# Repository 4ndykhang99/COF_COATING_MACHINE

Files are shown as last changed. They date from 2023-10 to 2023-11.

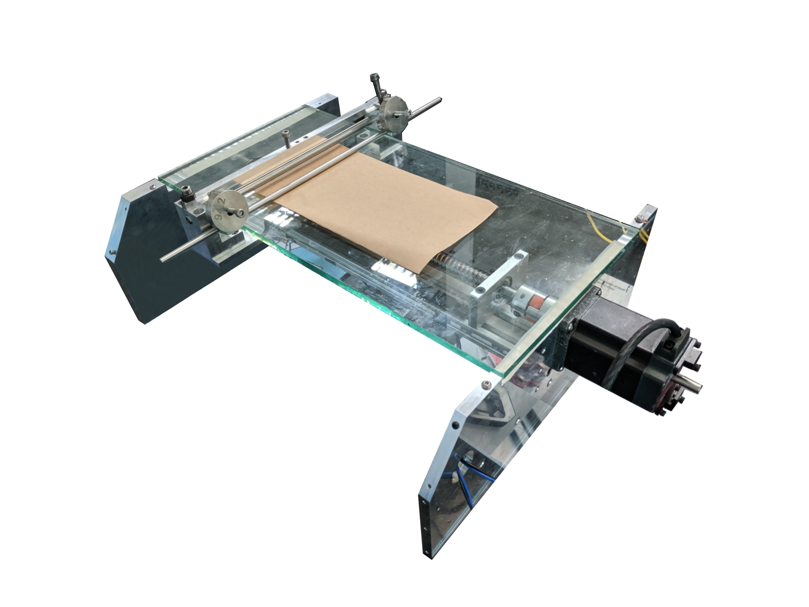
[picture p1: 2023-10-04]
3. Report/23_02_2023 - Introductrion about Lab Coating _ COF machine/1.png

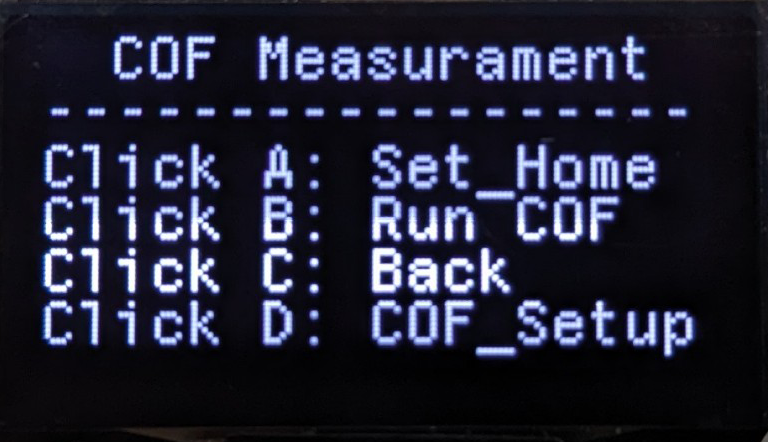
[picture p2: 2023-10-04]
4. Hình/HMI/5.png

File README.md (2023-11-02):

# COF_COATING_MACHINE
Included code, PCB, Software for COF &amp; Coating machine

## 11/2/2023
- Ghi nhận các lỗi:
    - Trôi công tắc hành trình trong chế độ COF.
    - Khi sử dụng COFcontroller.exe lưu đến mẫu 9 hoặc 10 sẽ bị lỗi ( chưa xác định), dữ liệu bị ngắn đi khi plot biểu đồ trên phần mềm, hoặc có thể do tốc độ của motor nhanh dần lên, càng đo về sau, biểu đồ plot lên càng ngắn.
    - Lỗi random: đo COF, bộ điều khiển trả về giá trị 0. Phần mềm lẫn board đọc về giá trị 0.
    - Idea về detect vị trí mỗi lần khởi động máy: khởi tạo một hàm scan_pos(), mỗi khi mất điện và bật hệ thống lại, hoặc mỗi lần reset, chương trình sẽ qua hàm scan_pos để nhận biết trạng thái của 2 công tắc hành trình như thế nào => giải quyết được vấn đề lưu vào bộ nhớ flash.
    - Lỗi liên quan đến cơ khí: Ở các màng mỏng có độ nhám cao, các kẹp base không thể giữ được hoàn toàn màng được đo, dẫn đến khi sled càng về cuối màng, màng càng bị nhăng -> kết quả đo sẽ sai lệch.
    - Anh Thiện suggest biểu đồ tự động detect chiều cao và tự động scale vừa với cửa sổ biểu đồ.

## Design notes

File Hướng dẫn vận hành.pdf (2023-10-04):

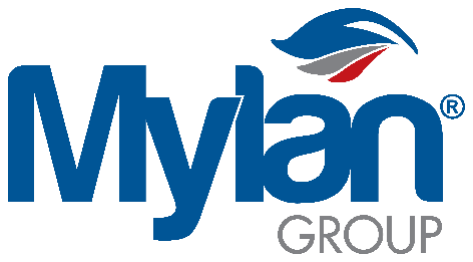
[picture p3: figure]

THIẾT BỊ ĐO HỆ SỐ MA SÁT VÀ TRÁNG MÀNG

MÃ THIẾT BỊ: MOP_CC2_0001

HƯỚNG DẪN VẬN HÀNH

Address: Longduc Industrial Park Travinh City, Travinh Province, Vietnam

Email: info@mylangroup.com

Phone: +84 -294-3846-997

## MỤC LỤC

THÔNG SỐ THIẾT BỊ | 3
CHỨC NĂNG MÁY | 3
CẤU TRÚC MÁY (COF) | 4
CẤU TRÚC MÁY ( COATING) | 5
GIÁ TRỊ LOADCELL | 6
KEYPAD | 6
ĐIỀU KHIỂN CHẾ ĐỘ TRÁNG GIẤY (COATING) | 7
ĐIỀU KHIỂN CHẾ ĐỘ ĐO HỆ SỐ MA SÁT (COF) | 7
CHANGE COF SPEED: ĐIỀU CHỈNH TỐC ĐỘ ĐO COF | 9
CHANGE COF DISTANCE: ĐIỀU CHỈNH KHOẢNG CÁCH ĐO COF | 9
SET ZER0: ĐƯA BỘ ĐIỀU KHIỂN LOADCELL VỀ ZERO | 9
HƯỚNG DẪN CHUẨN BỊ MẪU ĐO HỆ SỐ MA SÁT | 10
1. Cắt mẫu theo Sled: Chiều rộng là MD, dài là CD | 10
2. Cắt mẫu cho Base kẹp màng: chiều dài là MD, rộng là CD | 11
3. Đặt đúng mặt cần đo cho Sled | 11
4. Cố định một đầu màng trên Sled bằng băng keo dính | 12
5. Hoàn thành kẹp màng cho Sled | 12
HƯỚNG DẪN THỰC HIỆN ĐO HỆ SỐ MA SÁT | 13
1. Kẹp màng cho Base | 13
2. SetHome cho base | 13
3.Bắt đầu đo COF | 14
ĐIỀU KHIỂN MÁY COF COATING THÔNG QUA MÁY TÍNH | 15
1. Cài đặt phần mềm: | 15
2. Cách sử dụng chương trình | 15
3. Chế độ COATING | 15
4. Chế độ đo COF | 17
XEM KẾT QUẢ VÀ XUẤT PDF | 19
MÔ TẢ KẾT QUẢ ĐO HỆ SỐ MA SÁT | 20
1. STATIC | 20
2. KINETIC | 20

THÔNG SỐ THIẾT BỊ

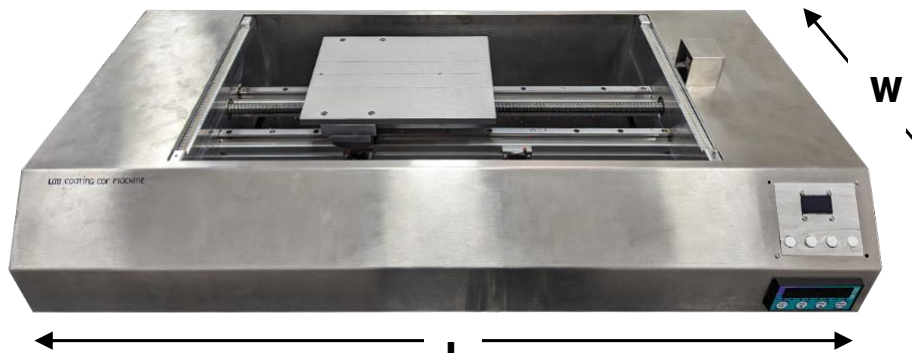
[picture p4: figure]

Điện áp đầu vào | 220VAC, 50/60Hz, 5amp
Nhiệt độ vận hành | 16 – 70 Độ C
Tốc độ | 0.1 – 4m/ phút
Khối lượng Sled | 200g
Thông số kích thước thân máy | 950x550x165mm (LxWxH)
Thông số base đặt màng COF | 250x200mm (LxW)
Thông số base Coating | 600x285mm (LxW)

CHỨC NĂNG MÁY

- Tích hợp tính năng Coating và đo hệ số ma sát trên cùng thiết bị.
- Màn hình hiển thị trực quan, dễ dàng điều khiển.
- Trang bị LoadCell tải trọng 600g với độ lệch chuẩn 0.2%.
- Có khả năng thu thập dữ liệu đo hệ số ma sát và xuất PDF thông qua truyền thông USBCDC.
- Hỗ trợ phần mềm điều khiển và thu thập dữ liệu thông qua máy tính.

H

L

CẤU TRÚC MÁY (COF)

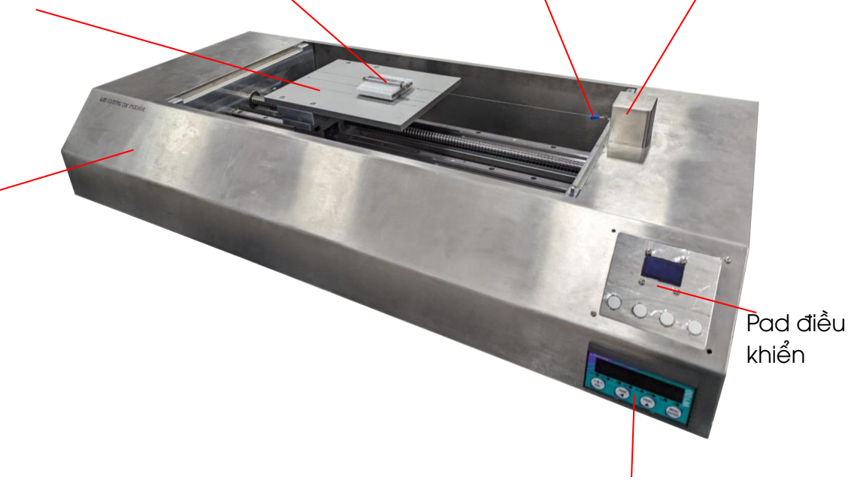
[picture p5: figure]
Pad điều khiển

- Switch nguồn: nằm phía sau Cover, dùng để bật tắt nguồn điện cho máy.
- Sled: Bao gồm khối vuông bao bởi Foam sốp với tổng khổi lượng 200g, dùng để gá màng vào và trượt trên màng cùng loại kẹp trên base kẹp màng COF.
- LoadCell: Đo lực kéo khi đang xác định hệ số ma sát của các tấm màng.
- Bộ điều khiển LoadCell: Thiết bị dùng để calib và chuyển đổi năng lượng nhận được từ LoadCell sang khối lượng.
- Pad điều khiển: Bao gồm 4 nút nhấn và một màn hình hiển thị, dùng để điều khiển và hiện thị công năng đang thực thi.
- Cover: Tấm kim loại bảo vệ và cách ly các thiết bị bên trong.

Sled

Dây kéo Sled

Base kẹp
màng COF

Cover

Loadcell

Bộ điều khiển
Loadcell

CẤU TRÚC MÁY ( COATING)

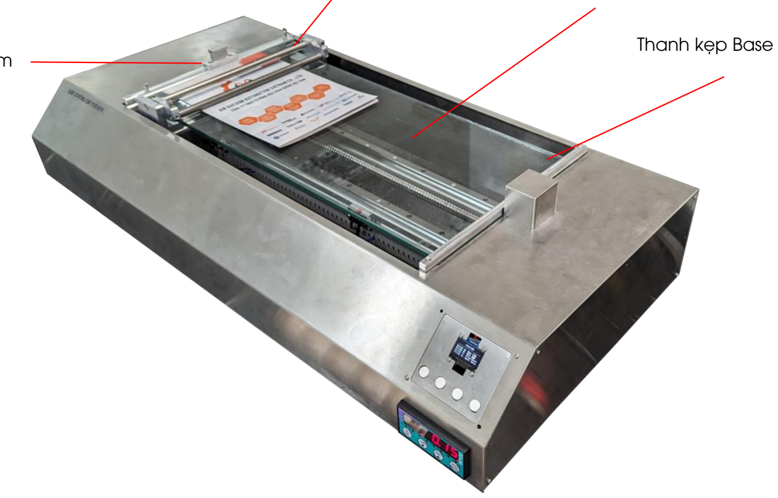
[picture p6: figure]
Thanh kẹp Base

- Thanh kẹp Film: Gồm có một dãy ron cao su và lò xo 2 bên, giúp thanh kim loại có thể đè, nén và giữ bề mặt Film cần coat không bị chạy.
- Module mayer bar: là bộ phận liên kết thanh trượt vitme với thanh mayer bar của máy.
- Coating Base: là vị trí đặt màng film cần coat, bề mặt làm bằng thủy tinh nên có độ nhẵn cao, nhược điểm dễ vỡ.
- Thanh kẹp Base: có 2 thanh kẹp base, giúp giữ Coating base ở 2 đầu.

Module mayer bar

Thanh kẹp Film

Coating Base

GIÁ TRỊ LOADCELL

- Giá trị được hiển thị trên Bộ điều khiển LoadCell, chính là giá trị qui đổi lực được kéo từ LoadCell.
- Giá trị an toàn mà LoadCell trên máy đo hệ số ma sát có thể kéo được không quá 600g.
- Nếu vượt ngưỡng giá trị an toàn, LoadCell có thể bị biến dạng, khiến các lần đo tiếp theo không đạt độ chính xác như ban đầu.

KEYPAD

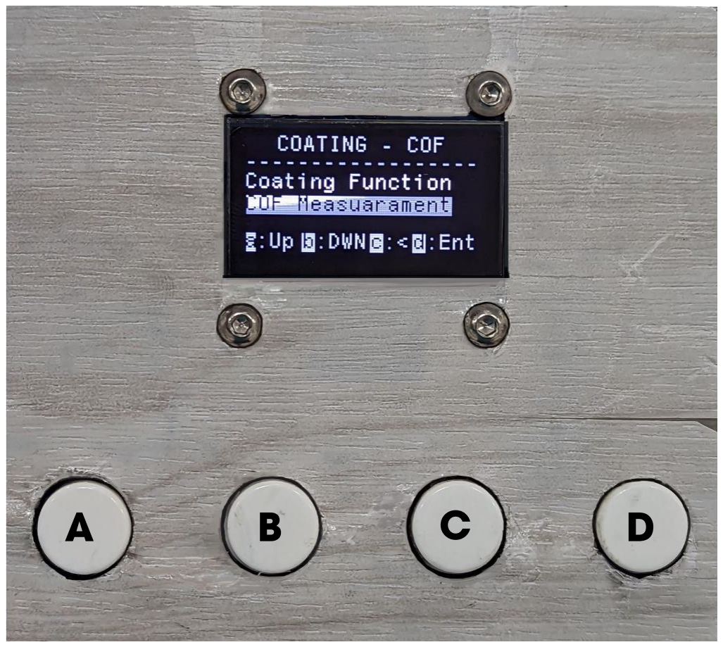
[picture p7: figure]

- KeyPad bao gồm màn hình Oled 1.3 inch và 4 nút nhấn A, B, C, D.
- Tùy vào từng giao diện điều khiển trên màn hình Oled mà các nút nhấn sẽ có các chức năng khác nhau.

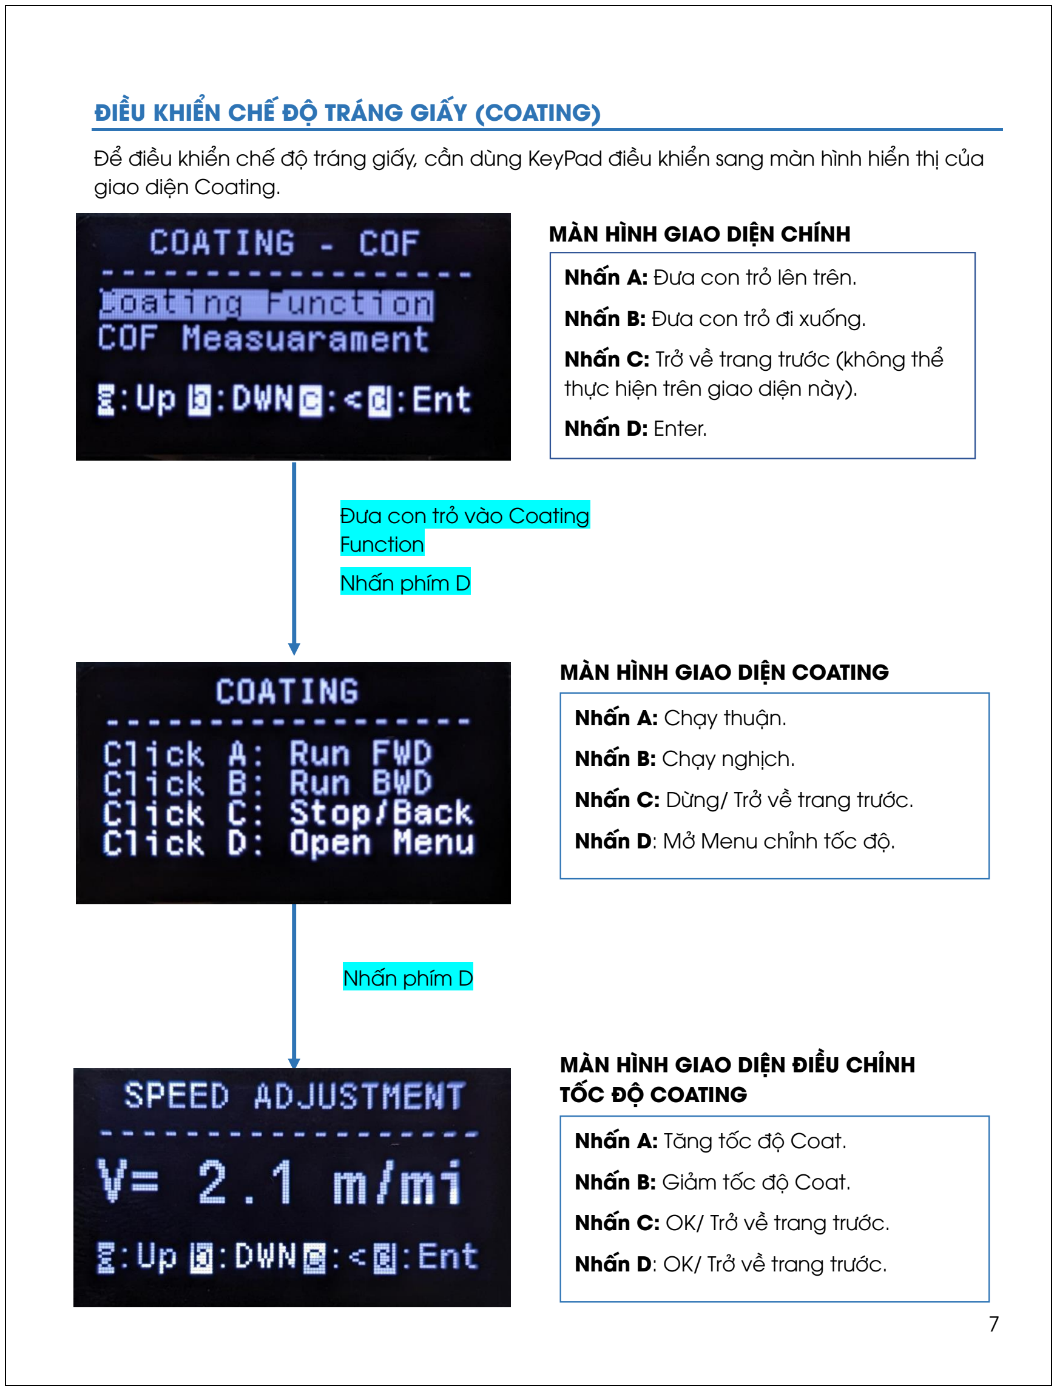
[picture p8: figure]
ĐIỀU KHIỂN CHẾ ĐỘ TRÁNG GIẤY (COATING); giao diện Coating.; Nhấn A: Đưa con trỏ lên trên.; Nhấn B: Đưa con trỏ đi xuống.; Nhấn C: Trở về trang trước (không thể; thực hiện trên giao diện này).; Nhấn D: Enter.; Nhấn A: Chạy thuận.; Nhấn B: Chạy nghịch.; Nhấn C: Dừng/ Trở về trang trước.; Nhấn D: Mở Menu chỉnh tốc độ.; MÀN HÌNH GIAO DIỆN CHÍNH; Nhấn phím D; MÀN HÌNH GIAO DIỆN COATING; MÀN HÌNH GIAO DIỆN ĐIỀU CHỈNH; TỐC ĐỘ COATING; Nhấn A: Tăng tốc độ Coat.; Nhấn B: Giảm tốc độ Coat.; Nhấn C: OK/ Trở về trang trước.; Nhấn D: OK/ Trở về trang trước.; Đưa con trỏ vào Coating; Function

Để điều khiển chế độ tráng giấy, cần dùng KeyPad điều khiển sang màn hình hiển thị của

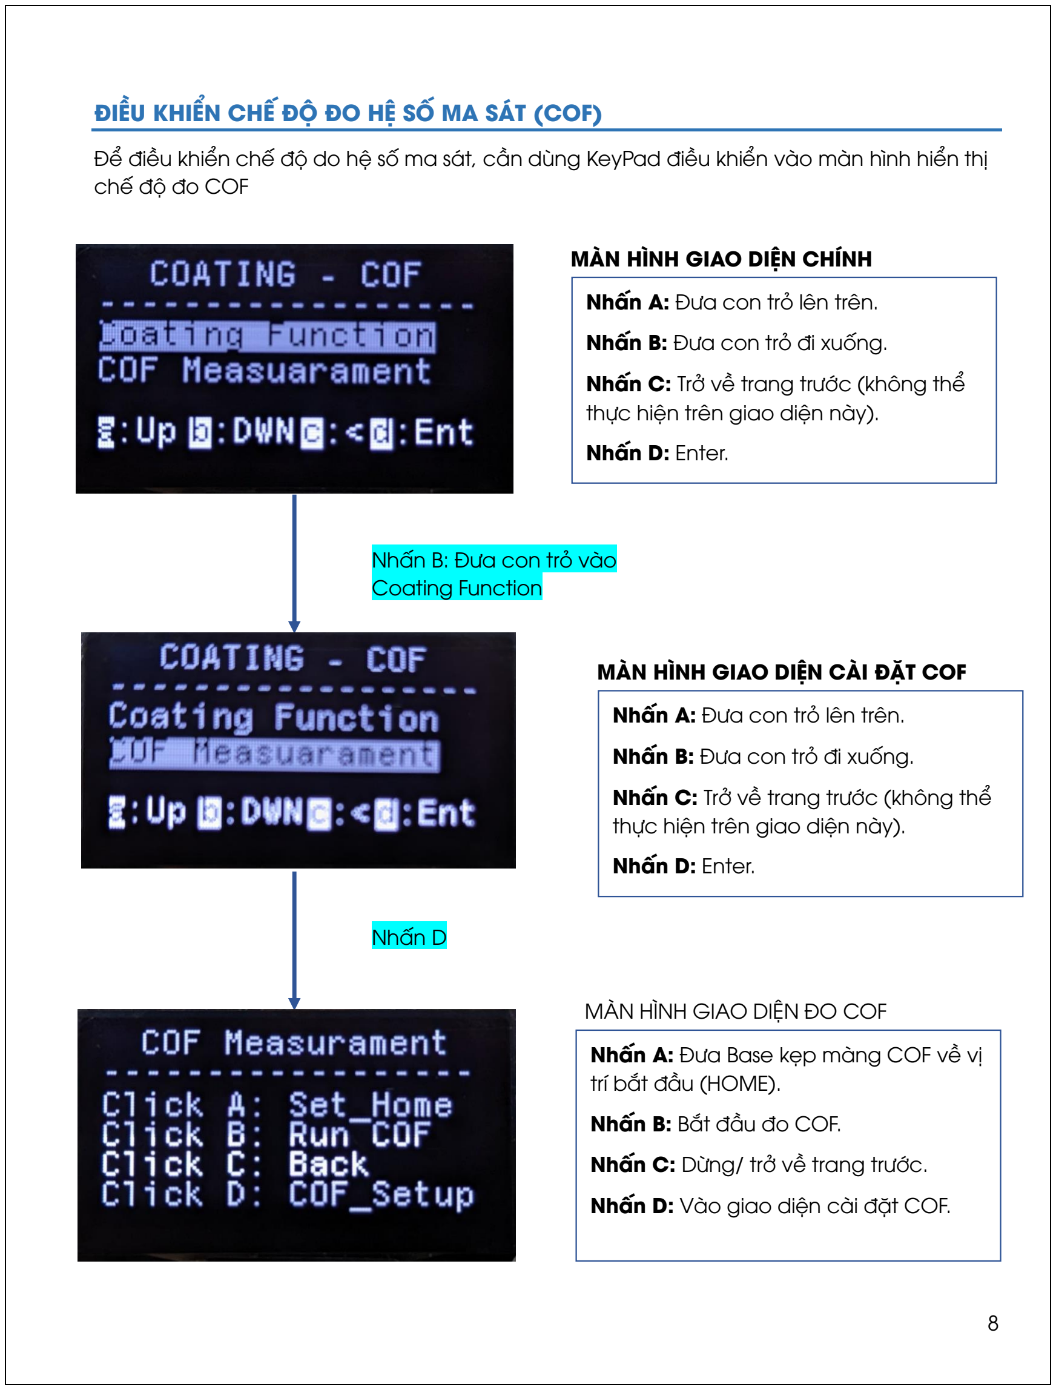
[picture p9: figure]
ĐIỀU KHIỂN CHẾ ĐỘ ĐO HỆ SỐ MA SÁT (COF); chế độ đo COF; MÀN HÌNH GIAO DIỆN CHÍNH; Nhấn A: Đưa con trỏ lên trên.; Nhấn B: Đưa con trỏ đi xuống.; Nhấn C: Trở về trang trước (không thể; thực hiện trên giao diện này).; Nhấn D: Enter.; Nhấn B: Đưa con trỏ vào; Coating Function; Nhấn D; Nhấn A: Đưa Base kẹp màng COF về vị; trí bắt đầu (HOME).; Nhấn B: Bắt đầu đo COF.; Nhấn C: Dừng/ trở về trang trước.; Nhấn D: Vào giao diện cài đặt COF.; MÀN HÌNH GIAO DIỆN ĐO COF; MÀN HÌNH GIAO DIỆN CÀI ĐẶT COF

Để điều khiển chế độ do hệ số ma sát, cần dùng KeyPad điều khiển vào màn hình hiển thị

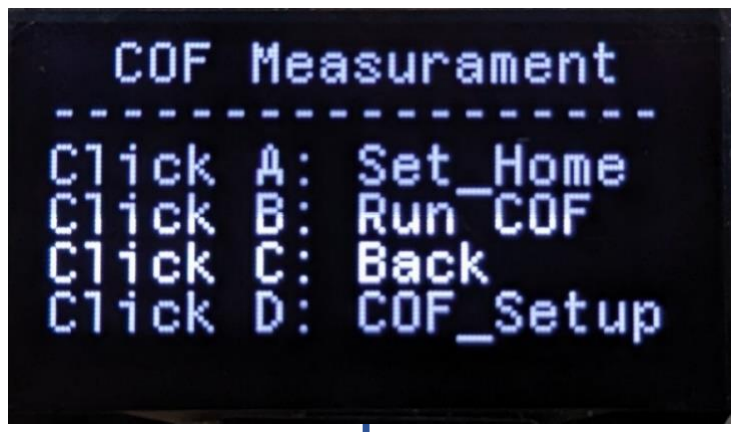
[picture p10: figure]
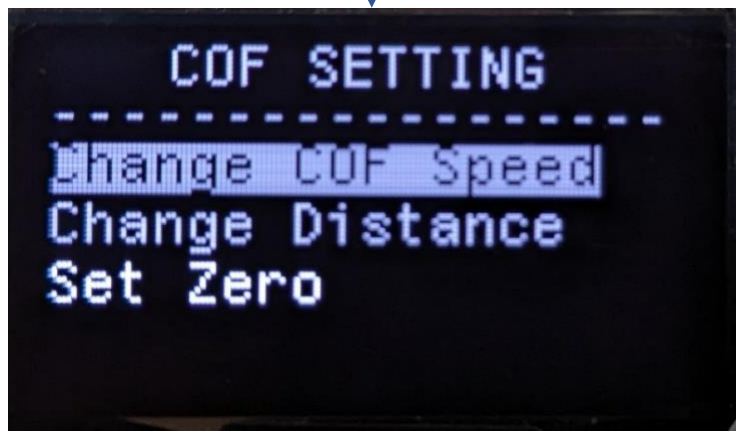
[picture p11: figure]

CHANGE COF SPEED: ĐIỀU CHỈNH TỐC ĐỘ ĐO COF

- Cách thức vào giống như điều chỉnh tốc độ Coating.
- Có 3 mức tốc độ: 0.10, 0.15 (Mặc định), 0.20 m/phút.

CHANGE COF DISTANCE: ĐIỀU CHỈNH KHOẢNG CÁCH ĐO COF

- Cách thức vào giống như điều chỉnh tốc độ Coating.
- Có 3 mức khoảng cách: 130 (Mặc định),140, 150 mm
SET ZER0: ĐƯA BỘ ĐIỀU KHIỂN LOADCELL VỀ ZERO

Sử dụng trong trường hợp khi chuẩn bị đo COF (dây kéo sled không căng) mà LoadCell đo được khác 0.

Lưu ý: Khi SetZero, dây kéo sled phải lỏng, chùng, không được căng.

Nhấn A: Đưa Base kẹp màng COF về vị trí bắt đầu (HOME).

Nhấn B: Bắt đầu đo COF.

Nhấn C: Dừng/ Trở về trang trước.

Nhấn D: Vào giao diện cài đặt COF.

MÀN HÌNH GIAO DIỆN ĐO COF

Nhấn D

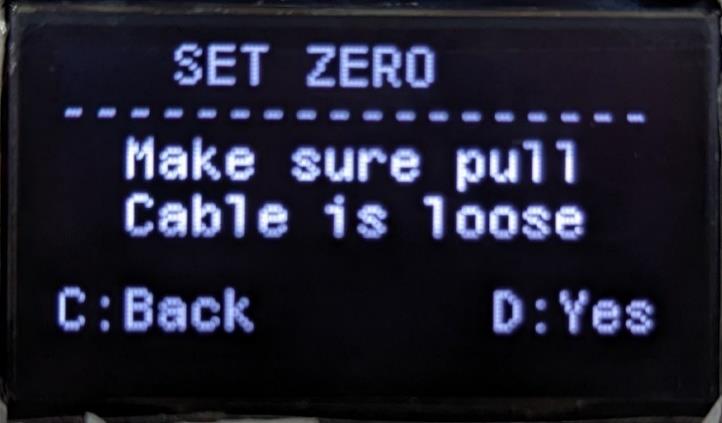
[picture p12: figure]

- Sau khi SetZero, hệ thống sẽ tự khởi động lại để bảo đảm mọi thứ hoạt động tốt nhất.

HƯỚNG DẪN CHUẨN BỊ MẪU ĐO HỆ SỐ MA SÁT

### 1. Cắt mẫu theo Sled

- Chú ý: tránh động tay vào phần cần đo để hạn chế tạp chất từ tay dính lên bề mặt.
- Quan trọng: Chiều rộng dưỡng Sled là MD, chiều dài là CD.

MÀN HÌNH GIAO DIỆN SETZERO

Nhấn C: Trở về trang trước, hủy bỏ SetZero

Nhấn D: Đã kiểm tra dây kéo Sled và đồng ý SetZero.

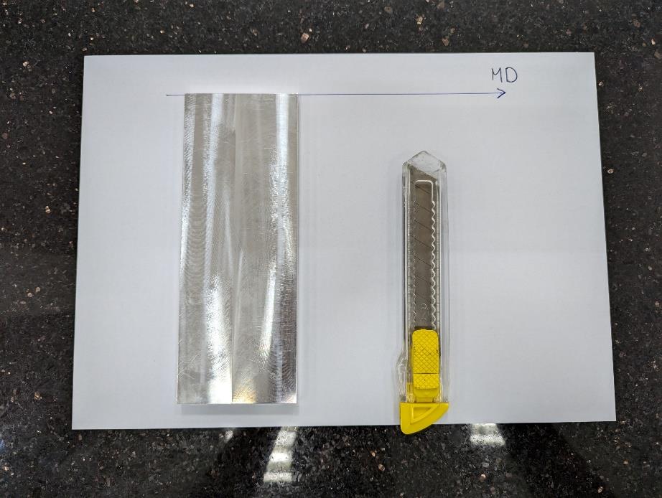
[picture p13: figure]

### 2. Cắt mẫu cho Base kẹp màng

- Chú ý: tránh động tay vào phần cần đo để hạn chế tạp chất từ tay dính lên bề mặt.
- Quan trọng: Chiều dài là MD chiều rộng là CD

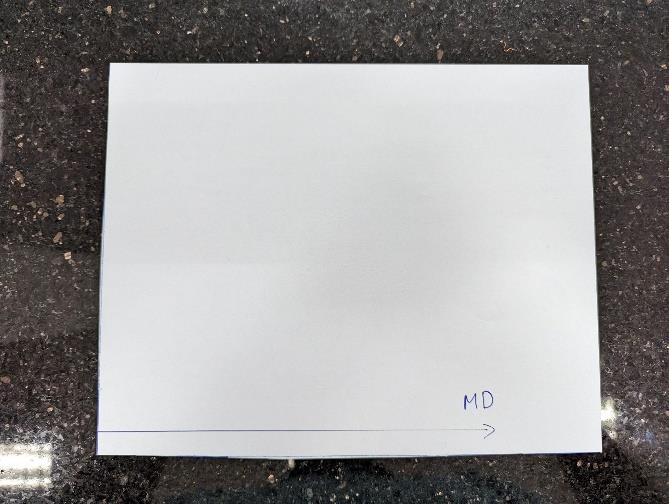
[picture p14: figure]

### 3. Đặt đúng mặt cần đo cho Sled

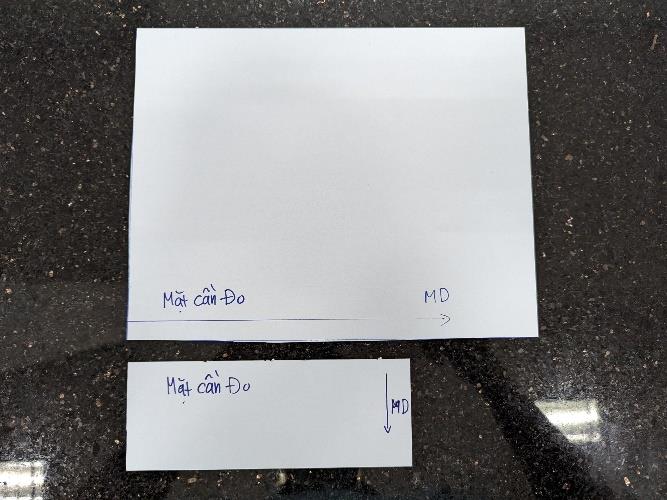
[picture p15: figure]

Khi đo COF, 2 bề mặt cần đo sẽ trực tiếp ma sát với nhau, vì thế màng kẹp vào Sled phải được xoay xuống dưới.

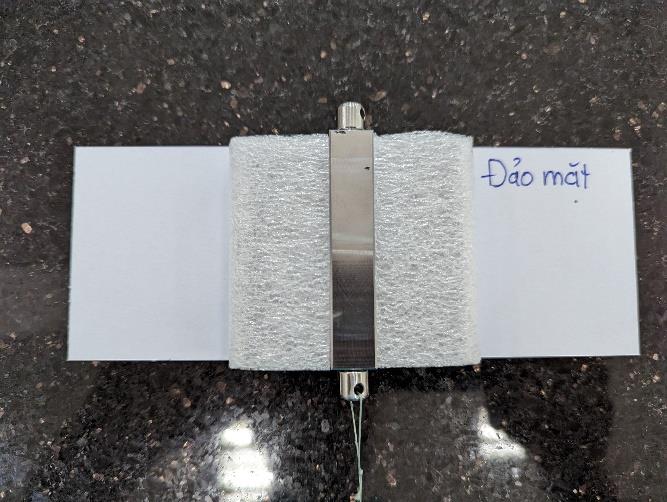
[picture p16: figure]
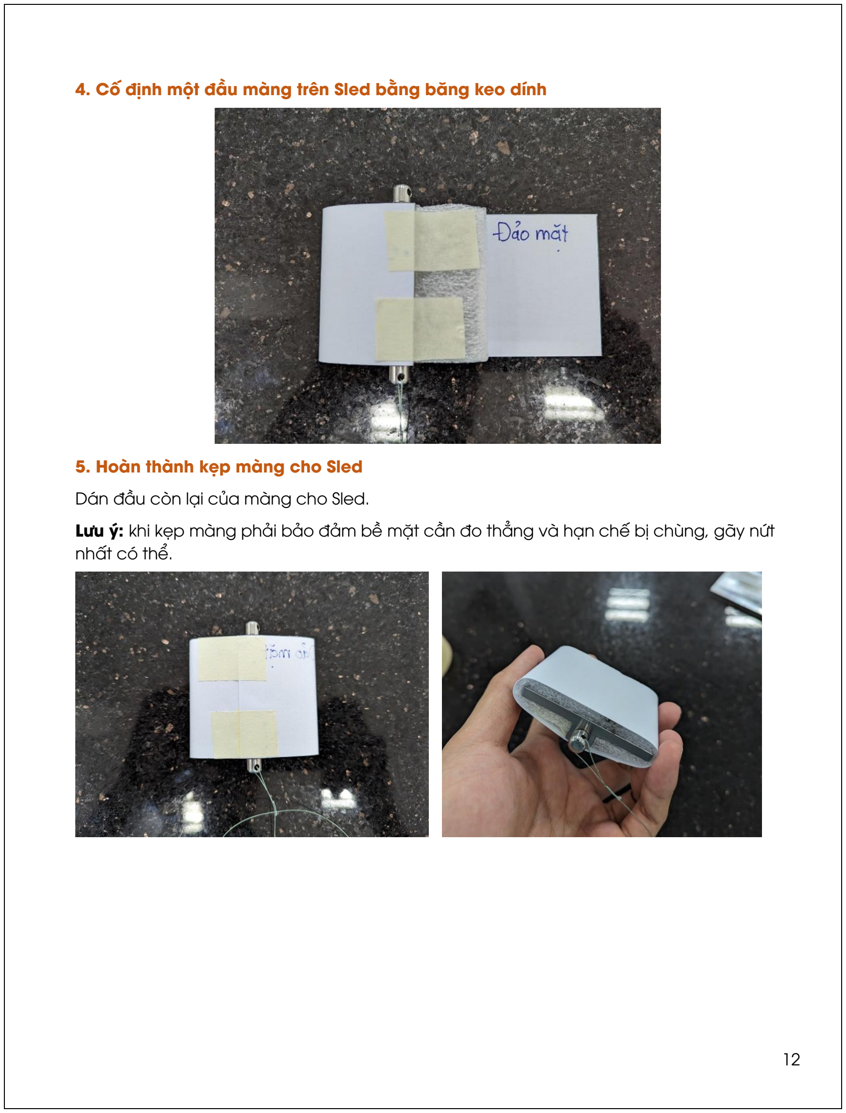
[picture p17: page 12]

### 4. Cố định một đầu màng trên Sled bằng băng keo dính

### 5. Hoàn thành kẹp màng cho Sled

Dán đầu còn lại của màng cho Sled.

Lưu ý: khi kẹp màng phải bảo đảm bề mặt cần đo thẳng và hạn chế bị chùng, gãy nứt nhất có thể.

HƯỚNG DẪN THỰC HIỆN ĐO HỆ SỐ MA SÁT

### 1. Kẹp màng cho Base

Dùng 4 kẹp cố định màng trên Base.

Lưu ý: Khi kẹp màng trên Base, bảo đảm 4 kẹp phải đồng đều, căng màng thẳng nhất có thể, để tránh hiện tượng chùng màng khi kéo Sled.

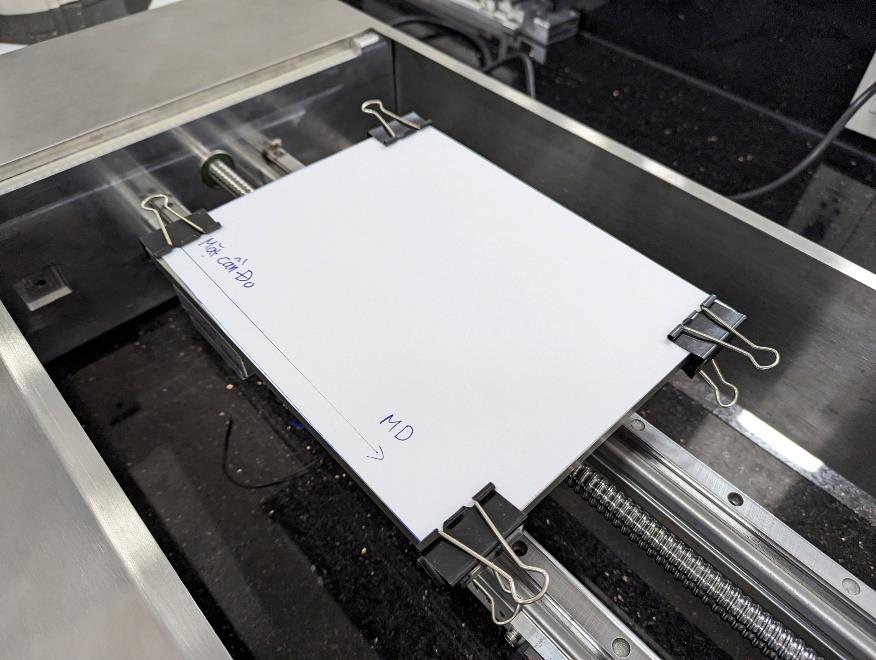
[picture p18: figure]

### 2. SetHome cho base

Dùng KeyPad vào giao diện đo hệ số ma sát, bấm SetHome để đưa base về vị trí bắt đầu đo.

*Tùy thuộc vào giá trị COF Distance trong phần COF Setting mà vị trí home của base sẽ dài hoặc ngắn khác nhau.

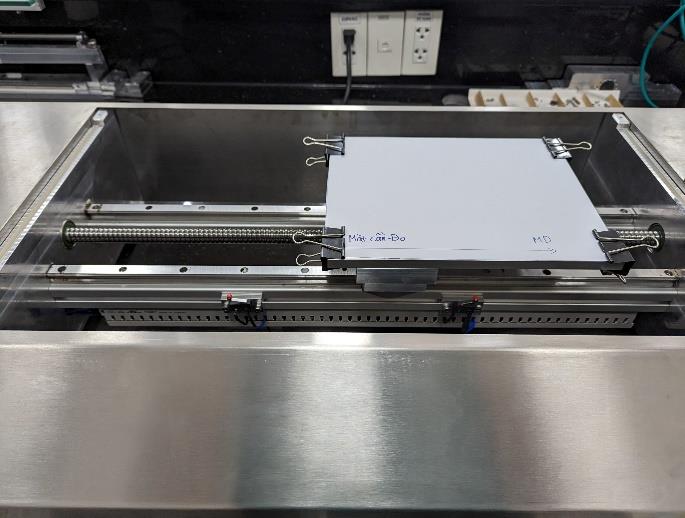
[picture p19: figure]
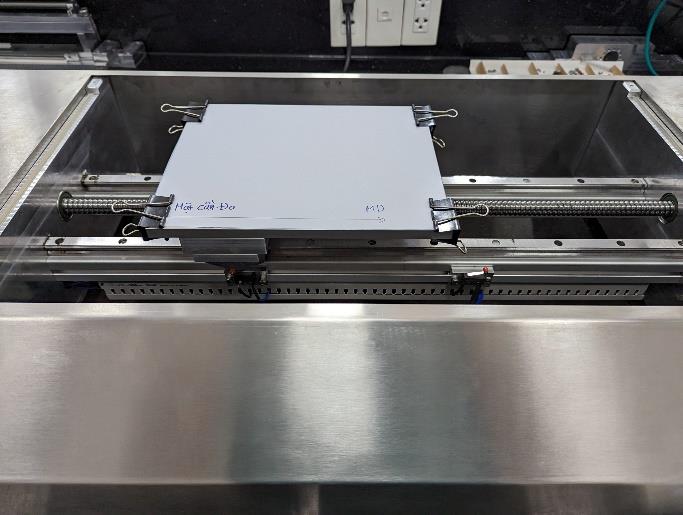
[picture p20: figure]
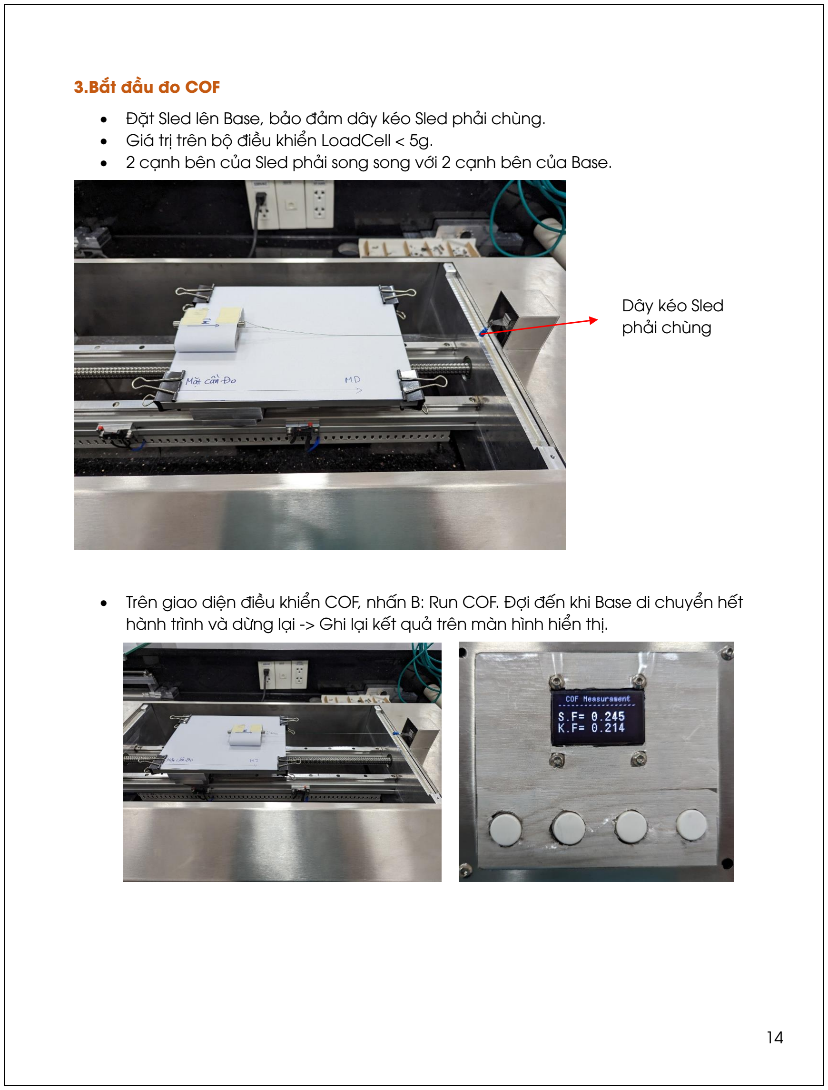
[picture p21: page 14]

3.Bắt đầu đo COF

- Đặt Sled lên Base, bảo đảm dây kéo Sled phải chùng.
- Giá trị trên bộ điều khiển LoadCell < 5g.
- 2 cạnh bên của Sled phải song song với 2 cạnh bên của Base.
- Trên giao diện điều khiển COF, nhấn B: Run COF. Đợi đến khi Base di chuyển hết hành trình và dừng lại -> Ghi lại kết quả trên màn hình hiển thị.

Dây kéo Sled
phải chùng

ĐIỀU KHIỂN MÁY COF COATING THÔNG QUA MÁY TÍNH

### 1. Cài đặt phần mềm:

Tiến hành cài đặt 2 file trong thư mục cài đặt:

Setup.exe và STMicroelectronics Driver.exe.

### 2. Cách sử dụng chương trình

- Đầu tiên phải bảo đảm máy COF đã được kết nối thông qua cổng USB của máy tính.
- Tiếp theo mở phần mềm COF_Controller.exe, ta sẽ thấy cửa số xuất hiện như hình dưới:

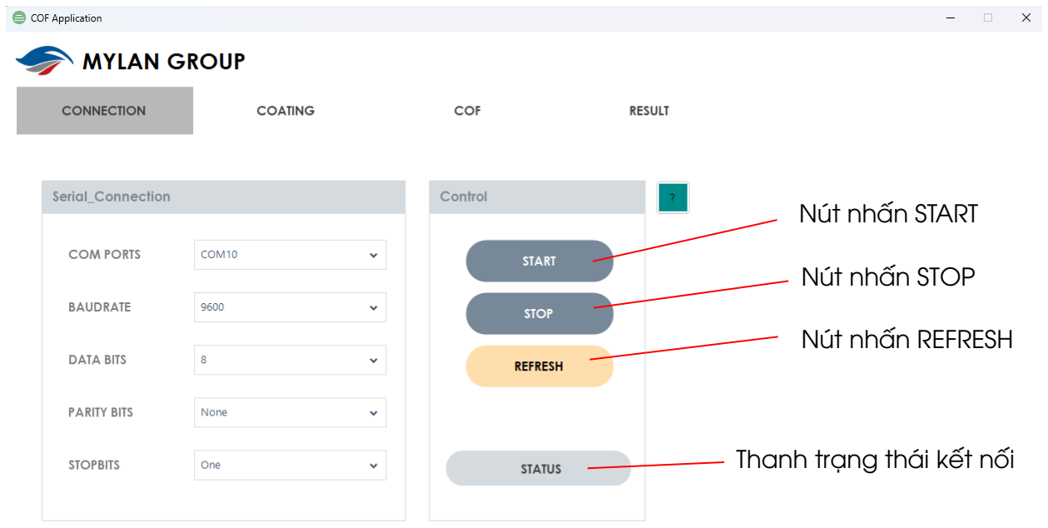
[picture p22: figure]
Nút nhấn START; Nút nhấn STOP; Nút nhấn REFRESH; Thanh trạng thái kết nối

- | Nhấn nút | để phần mềm tự động cập nhật cổng USB đang kết nói với
máy COF tại ListBox COM PORTS.
- | Sau đó nhấn nút | để PC kết nối với máy COF.
- Sau khi kết nối thành công, thanh STATUS sẽ chuyển sang màu xanh.
- | Để ngắt kết nối với máy COF, nhấn | .

### 3. Chế độ COATING

Chuyển sang thẻ | để vào giao diện | :

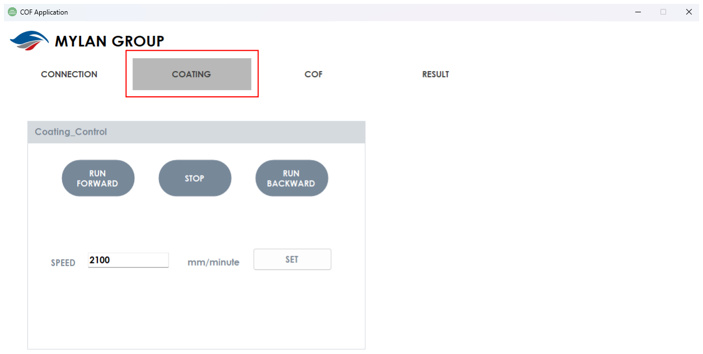
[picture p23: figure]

- Khi bắt đầu kết nối với máy COF, các thông số hiện đang được set trên máy COF sẽ được cập nhật lên phần mềm COF Controller, cụ thể ở tab COATING, thông số

đã được đồng bộ với máy.
- Để set tốc độ coat, nhập từ bàn phím vào TextBox SPEED, sau đó gõ Enter hoặc ấn
- | Sử dụng 3 nút nhấn | để điều khiển chạy thuận
| nghịch cho đầu tráng của máy.

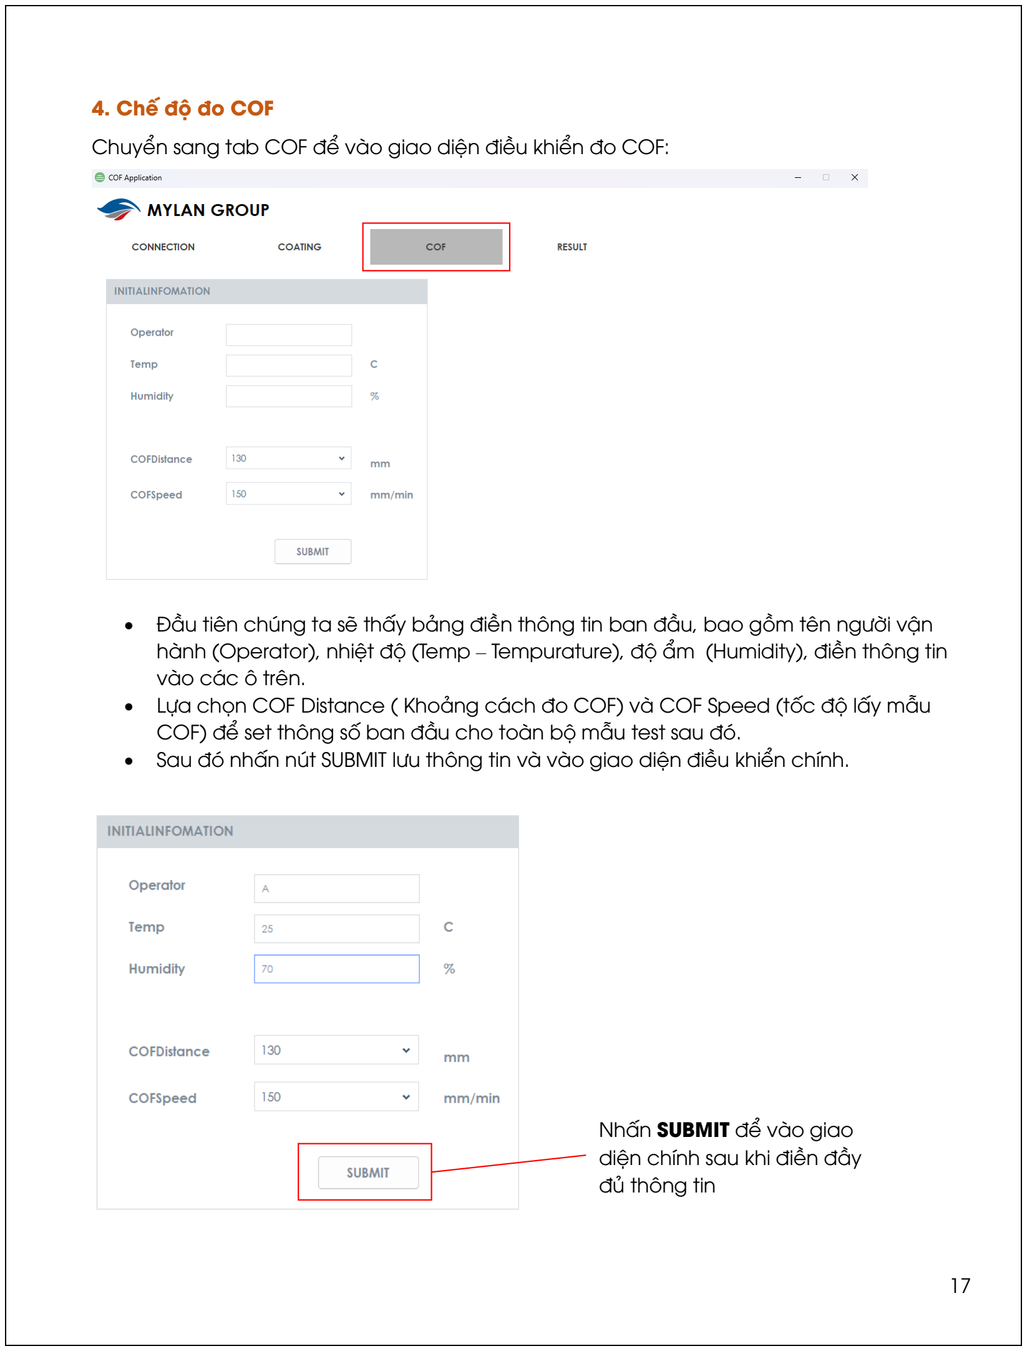
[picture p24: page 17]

### 4. Chế độ đo COF

Chuyển sang tab COF để vào giao diện điều khiển đo COF:

- Đầu tiên chúng ta sẽ thấy bảng điền thông tin ban đầu, bao gồm tên người vận hành (Operator), nhiệt độ (Temp – Tempurature), độ ẩm (Humidity), điền thông tin vào các ô trên.
- Lựa chọn COF Distance ( Khoảng cách đo COF) và COF Speed (tốc độ lấy mẫu COF) để set thông số ban đầu cho toàn bộ mẫu test sau đó.
- Sau đó nhấn nút SUBMIT lưu thông tin và vào giao diện điều khiển chính.

Nhấn SUBMIT để vào giao
diện chính sau khi điền đầy đủ thông tin

Giao diện điều khiển đo COF chính:

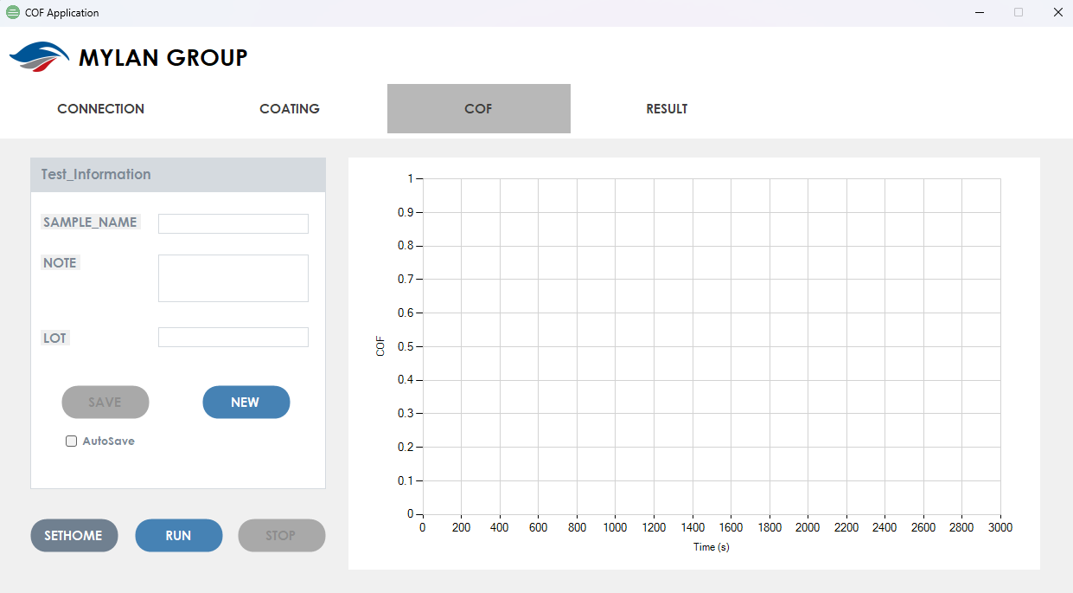
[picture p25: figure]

- | Nhấn | trước khi đo, đề Base về vị trí đo
- | Sau đó bấm Phím | Để bắt đầu đo COF.
- Trong quá trình đo, kết quả của từng Data Point sẽ được vẽ lên đồ thị trong giao diện.
- | Để lưu kết quả đo, bấm phím | , mọi thông tin đã lưu sẽ được hiển thị bên
Tab | .
- | Để chương trình tự động lưu sau mỗi lần đo, tích vào | .
- | Bấm | để tạo hồ sơ đo mới.
- Lưu ý: người dùng nên cập nhật Sample Name, Note và Lot trước khi đo COF để có thông tin tương ứng với lần đo kế tiếp.

XEM KẾT QUẢ VÀ XUẤT PDF

- | Ở Tab | , các kết quả đo sẽ được thống kê theo thứ tự đo.
- | Để xuất file PDF của toàn bộ thông tin đo, bấm vào biểu tượng | trên góc phải
màn hình.

MÔ TẢ KẾT QUẢ ĐO HỆ SỐ MA SÁT

### 1. STATIC

Static COF hay hệ số ma sát tĩnh, là lực cần thiết ban đầu để thắng được sự đứng yên của Sled và bắt đầu chuyển động. Static COF trong hệ thống được xác định là đỉnh đầu tiên của chuỗi dữ liệu được ghi nhận.

Static COF được tính theo công thức:

### 2. KINETIC

Kinetic COF còn được hiểu là ma sát động, là trung bình cộng của tổng lực thu được từ chuỗi dữ liệu sau Static COF.

Kinatic COF được tính theo công thức:

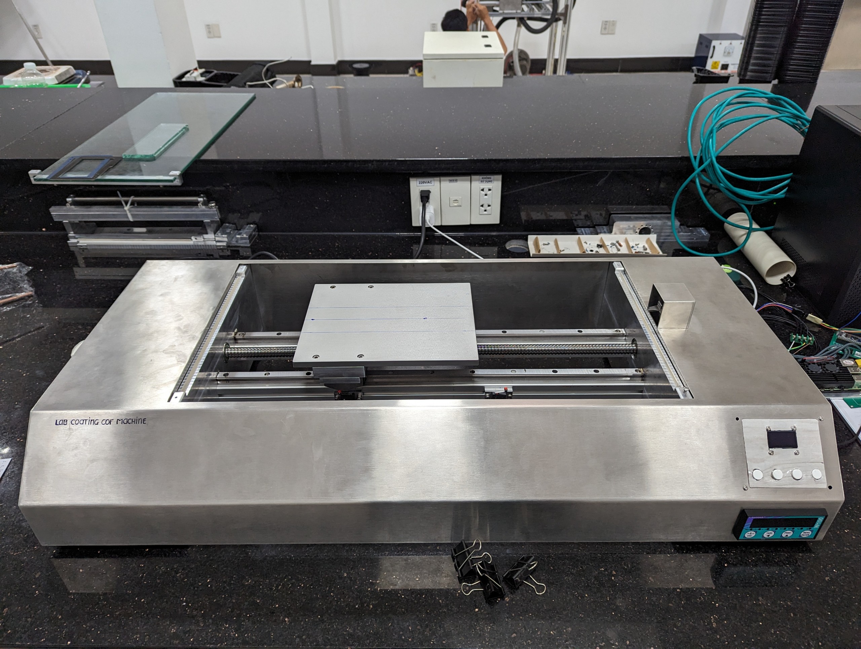
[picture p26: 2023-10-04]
4. Hình/COF.jpg

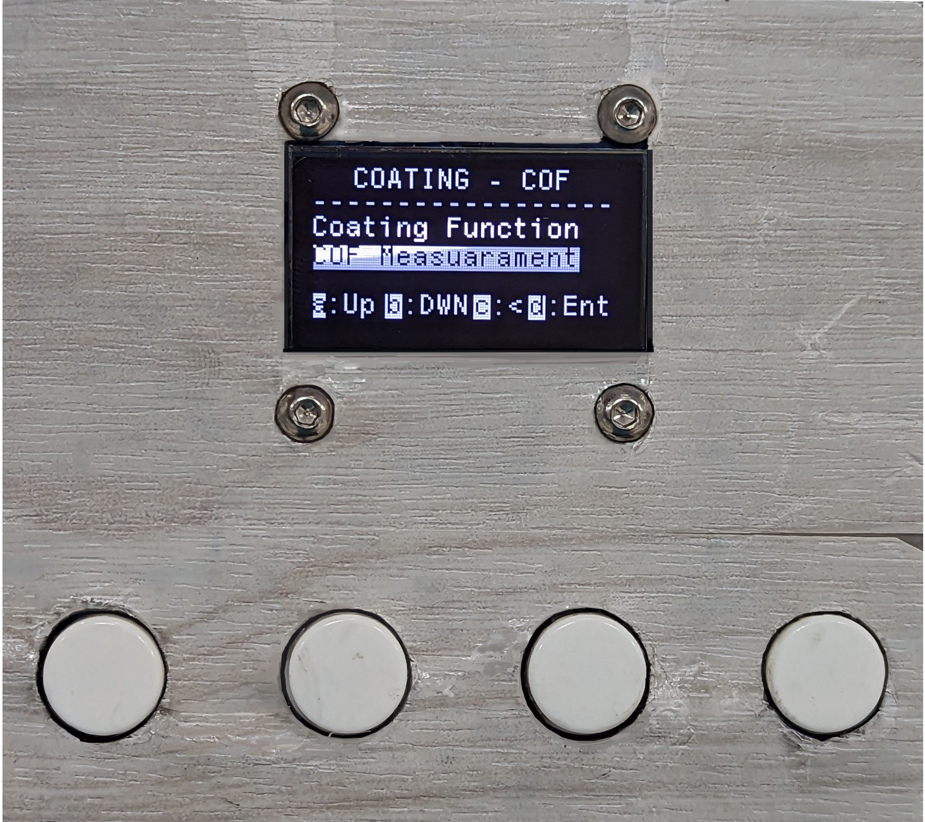
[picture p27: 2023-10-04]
4. Hình/HMI/Keypad.png

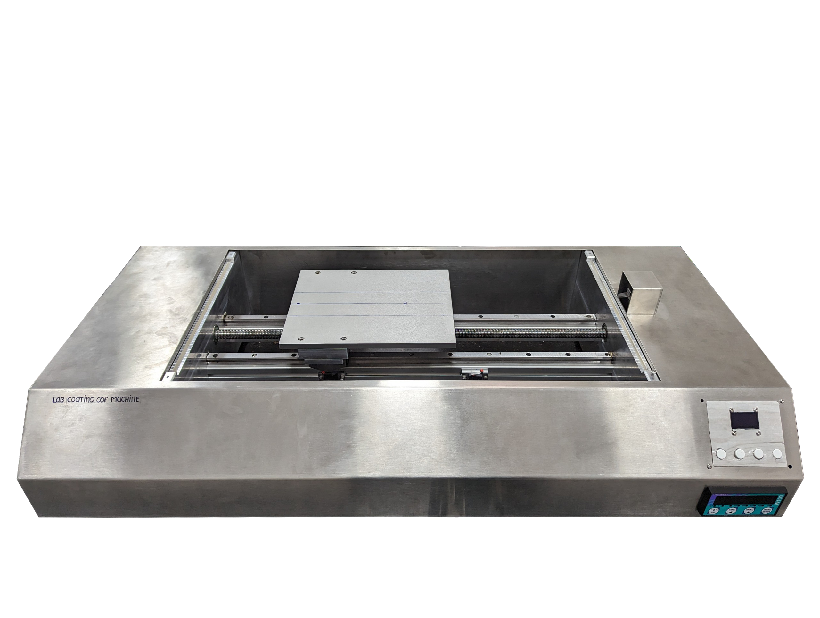
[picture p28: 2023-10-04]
4. Hình/COF.png

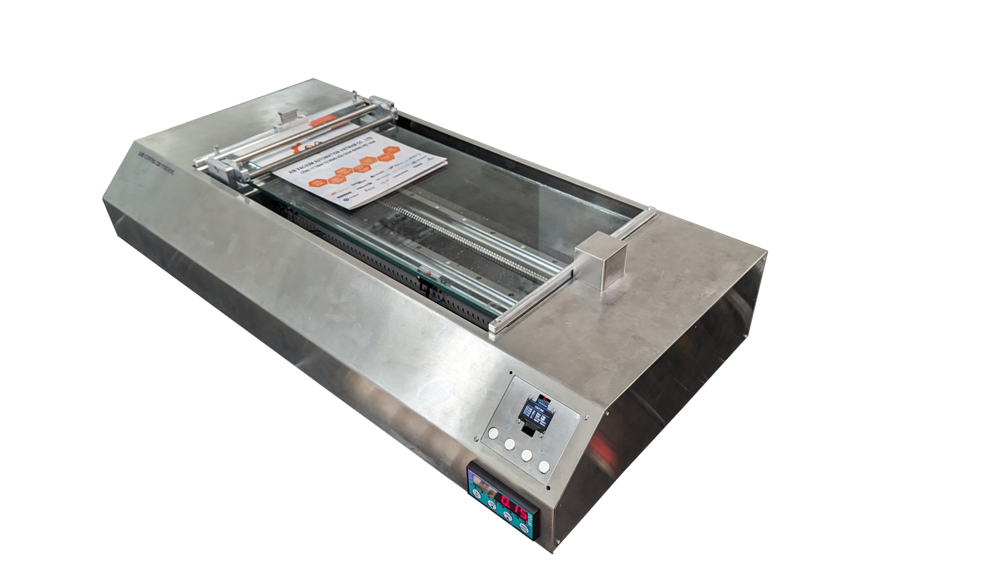
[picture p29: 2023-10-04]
4. Hình/Coating1.png

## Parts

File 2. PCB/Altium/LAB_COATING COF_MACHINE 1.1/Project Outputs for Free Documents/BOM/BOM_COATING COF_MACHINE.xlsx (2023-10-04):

Description | Designator | Footprint | LibRef | Quantity
CAP CER 22UF 6.3V X5R 0603 | C1, C2, C3, C4, C13, C14 | C 0603 | CAP CER 22UF 6.3V X5R 0603 - GRM188R60J226MEA0D | 6
Multilayer Ceramic Capacitors MLCC - SMD/SMT | C5, C6, C7, C8, C15 | CAPC1608X95N | CAP CER 0.1UF 10V X7R 0603 - C0603C104K8RACTU | 5
CAP CER 0.1UF 50V X7R 0603 | C9, C11 | C 0603 | CAP CER 0.1UF 50V X7R 0603 - ESD35C104K4T2A-24 | 2
CAP CER 10UF 50V Y5V 1210 | C10 | CAPC3225X290N | CAP CER 10UF 50V Y5V 1210 - 12105G106ZAT2A | 1
CAP CER 56PF 50V C0G/NPO 0402 | C12 | CAPC1005X55N | CAP CER 56PF 50V C0G/NPO 0402 - CC0402JRNPO9BN560 | 1
DIODE SCHOTTKY 30V 150MA SOT23 | D1, D2, D3, D4 | SOT95P240X120-3N | DIODE SCHOTTKY 30V 150MA SOT23 - BAT54S | 4
FIXED IND 4.7UH 5.5A 40 MOHM SMD | L1 | INDM6965X300N | IND 4.7UH 5.5A 40 MOHM SMD - IHLP2525CZER4R7M01 | 1
TRANS NPN 45V 0.8A SOT23-3 | Q1, Q2 | SOT95P237X111-3N | TRANS NPN 45V 0.8A SOT23-3 - BCW66GLT1G | 2
RES SMD 2.2K OHM 5% 1/2W 0805 | R1, R5, R13, R14, R15, R16 | RES 0805 | RES SMD 2.2K OHM 5% 1/2W 0805 - ERJ-P06J222V | 6
RES SMD 100K OHM 1% 1/10W 0603 | R2, R6 | Res 0603 | RES SMD 100K OHM 1% 1/10W 0603 - CRCW0603100KFKEA | 2
RES SMD 1K OHM 5% 1/10W 0603 | R3, R9 | ERJ3EKF1000V | RES SMD 1K OHM 5% 1/10W 0603 - ERJ-3GEYJ102V | 2
RES SMD 10K OHM 5% 1/10W 0603 | R4, R11 | ERJ3EKF1000V | RES SMD 10K OHM 5% 1/10W 0603 - ERJ3GEYJ103V | 2
RES 4.7K OHM 1% 1/10W 0603 | R7, R8, R10, R12, R19, R20 | Res 0603 | RES 4.7K OHM 1% 1/10W 0603 - RC0603FR-074K7L | 6
RES SMD 9.1K OHM 1% 1/10W 0603 | R17, R18 | Res 0603 | RES SMD 9.1K OHM 1% 1/10W 0603 - ERJ-3EKF9101V | 2
RES SMD 100K OHM 1% 1/10W 0402 | R21, R22 | ERJ2RKD1004X | RES SMD 100K OHM 1% 1/10W 0402 - ERJ2RKF1003X | 2
RES 93.1K OHM 1% 1/16W 0402 | R23 | RESC1005X40N | RES 93.1K OHM 1% 1/16W 0402 - RC0402FR-0793K1L | 1
RES SMD 30.1K OHM 1% 1/10W 0402 | R24 | ERJ2RKD1004X | RES SMD 30.1K OHM 1% 1/10W 0402 - ERJ-2RKF3012X | 1
Optoisolator Transistor Output 5000Vrms 1 Channel 4-SMD | U2, U3 | SOT254P975X400-4N | OPTOISOLATOR 5KV TRANS 4SMD - PC817X2NIP0F | 2
IC REG BUCK ADJUSTABLE 2A TSOT26 | U4 | SOT95P280X100-6N | IC REG BUCK ADJUSTABLE 2A TSOT26 - AP63300WU-7 | 1

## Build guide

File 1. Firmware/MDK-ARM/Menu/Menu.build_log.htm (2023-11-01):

µVision Build Log

Tool Versions:

IDE-Version: µVision V5.31.0.0
Copyright (C) 2020 ARM Ltd and ARM Germany GmbH. All rights reserved.
License Information: khang democt2022@gmail.com, khang, LIC=47GU5-GIEK7-Y8GFK-ZZ0MC-XVRYS-7G1YA
 
Tool Versions:
Toolchain:       MDK-ARM Plus  Version: 5.31.0.0
Toolchain Path:  C:\Keil_v5\ARM\ARMCC\Bin
C Compiler:      Armcc.exe V5.06 update 6 (build 750)
Assembler:       Armasm.exe V5.06 update 6 (build 750)
Linker/Locator:  ArmLink.exe V5.06 update 6 (build 750)
Library Manager: ArmAr.exe V5.06 update 6 (build 750)
Hex Converter:   FromElf.exe V5.06 update 6 (build 750)
CPU DLL:         SARMCM3.DLL V5.31.0.0
Dialog DLL:      DCM.DLL V1.17.3.0
Target DLL:      STLink\ST-LINKIII-KEIL_SWO.dll V3.0.7.0
Dialog DLL:      TCM.DLL V1.46.0.0

Project:

D:\1. JOB\3. Project\LAB_COATING_COF\COF_COATING_MACHINE\1. Firmware\MDK-ARM\Menu.uvprojx
Project File Date:  10/04/2023

Output:

*** Using Compiler 'V5.06 update 6 (build 750)', folder: 'C:\Keil_v5\ARM\ARMCC\Bin'
Build target 'Menu'
compiling main.c...
../Core/Inc/main.h(58): warning:  #1295-D: Deprecated declaration Main_Menu - give arg types
  void Main_Menu();
../Core/Inc/main.h(59): warning:  #1295-D: Deprecated declaration Speed_Menu - give arg types
  void Speed_Menu();
../Core/Inc/main.h(60): warning:  #1295-D: Deprecated declaration COF_Menu - give arg types
  void COF_Menu();
../Core/Inc/main.h(61): warning:  #1295-D: Deprecated declaration Coating_Menu - give arg types
  void Coating_Menu();
../Core/Inc/main.h(62): warning:  #1295-D: Deprecated declaration COF_Result - give arg types
  void COF_Result();
../Core/Inc/main.h(63): warning:  #1295-D: Deprecated declaration COF_Options - give arg types
  void COF_Options();
../Core/Inc/main.h(64): warning:  #1295-D: Deprecated declaration COF_Zero - give arg types
  void COF_Zero();
../Core/Inc/main.h(65): warning:  #1295-D: Deprecated declaration COF_Speed - give arg types
  void COF_Speed();
../Core/Inc/main.h(66): warning:  #1295-D: Deprecated declaration COF_Distance - give arg types
  void COF_Distance();
../Core/Inc/main.h(67): warning:  #1295-D: Deprecated declaration resetbutton - give arg types
  void resetbutton();
../Core/Inc/main.h(69): warning:  #1295-D: Deprecated declaration HMI_Coating - give arg types
  void HMI_Coating();
../Core/Inc/main.h(70): warning:  #1295-D: Deprecated declaration HMI_Speed_Adjustment - give arg types
  void HMI_Speed_Adjustment();
../Core/Inc/ssd1306.h(238): warning:  #1295-D: Deprecated declaration ssd1306_I2C_Init - give arg types
  void ssd1306_I2C_Init();
../Core/Inc/mylan.h(24): warning:  #1-D: last line of file ends without a newline
  #endif
../Core/Src/main.c(468): warning:  #188-D: enumerated type mixed with another type
  	SSD1306_Puts("COATING - COF",&Font_7x10,0x01);
../Core/Src/main.c(470): warning:  #188-D: enumerated type mixed with another type
  	SSD1306_Puts("--------------------",&Font_7x10,0x01);
../Core/Src/main.c(472): warning:  #188-D: enumerated type mixed with another type
  	SSD1306_Puts("Coating Function",&Font_7x10,Coating_function);
../Core/Src/main.c(474): warning:  #188-D: enumerated type mixed with another type
  	SSD1306_Puts("COF Measuarament",&Font_7x10,COF_Measurament);
../Core/Src/main.c(478): warning:  #188-D: enumerated type mixed with another type
  	SSD1306_Puts("a",&Font_7x10,0x00);
../Core/Src/main.c(480): warning:  #188-D: enumerated type mixed with another type
  	SSD1306_Puts(":Up",&Font_7x10,0x01);
../Core/Src/main.c(483): warning:  #188-D: enumerated type mixed with another type
  	SSD1306_Puts("b",&Font_7x10,0x00);
../Core/Src/main.c(485): warning:  #188-D: enumerated type mixed with another type
  	SSD1306_Puts(":DWN",&Font_7x10,0x01);
../Core/Src/main.c(488): warning:  #188-D: enumerated type mixed with another type
  	SSD1306_Puts("c",&Font_7x10,0x00);
../Core/Src/main.c(490): warning:  #188-D: enumerated type mixed with another type
  	SSD1306_Puts(":<",&Font_7x10,0x01);
../Core/Src/main.c(493): warning:  #188-D: enumerated type mixed with another type
  	SSD1306_Puts("d",&Font_7x10,0x00);
../Core/Src/main.c(495): warning:  #188-D: enumerated type mixed with another type
  	SSD1306_Puts(":Ent",&Font_7x10,0x01);
../Core/Src/main.c(567): warning:  #188-D: enumerated type mixed with another type
  	SSD1306_Puts("SPEED ADJUSTMENT",&Font_7x10,0x01);
../Core/Src/main.c(569): warning:  #188-D: enumerated type mixed with another type
  	SSD1306_Puts("--------------------",&Font_7x10,0x01);
../Core/Src/main.c(571): warning:  #188-D: enumerated type mixed with another type
  	SSD1306_Puts("V=",&Font_11x18,0x01);
../Core/Src/main.c(577): warning:  #188-D: enumerated type mixed with another type
  	SSD1306_Puts(V ,&Font_11x18,0x01);
../Core/Src/main.c(579): warning:  #188-D: enumerated type mixed with another type
  	SSD1306_Puts(".",&Font_11x18,0x01);
../Core/Src/main.c(582): warning:  #188-D: enumerated type mixed with another type
  	SSD1306_Puts(R ,&Font_11x18,0x01);
../Core/Src/main.c(584): warning:  #188-D: enumerated type mixed with another type
  	SSD1306_Puts("m/min",&Font_11x18,0x01);
../Core/Src/main.c(595): warning:  #188-D: enumerated type mixed with another type
  	SSD1306_Puts("a",&Font_7x10,0x00);
../Core/Src/main.c(597): warning:  #188-D: enumerated type mixed with another type
  	SSD1306_Puts(":Up",&Font_7x10,0x01);
../Core/Src/main.c(600): warning:  #188-D: enumerated type mixed with another type
  	SSD1306_Puts("b",&Font_7x10,0x00);
../Core/Src/main.c(602): warning:  #188-D: enumerated type mixed with another type
  	SSD1306_Puts(":DWN",&Font_7x10,0x01);
../Core/Src/main.c(605): warning:  #188-D: enumerated type mixed with another type
  	SSD1306_Puts("c",&Font_7x10,0x00);
../Core/Src/main.c(607): warning:  #188-D: enumerated type mixed with another type
  	SSD1306_Puts(":<",&Font_7x10,0x01);
../Core/Src/main.c(610): warning:  #188-D: enumerated type mixed with another type
  	SSD1306_Puts("d",&Font_7x10,0x00);
../Core/Src/main.c(612): warning:  #188-D: enumerated type mixed with another type
  	SSD1306_Puts(":Ent",&Font_7x10,0x01);
../Core/Src/main.c(620): warning:  #188-D: enumerated type mixed with another type
  	SSD1306_Puts("COATING",&Font_7x10,0x01);
../Core/Src/main.c(622): warning:  #188-D: enumerated type mixed with another type
  	SSD1306_Puts("--------------------",&Font_7x10,0x01);
../Core/Src/main.c(624): warning:  #188-D: enumerated type mixed with another type
  	SSD1306_Puts("Click A: Run FWD",&Font_7x10,0x01);
../Core/Src/main.c(626): warning:  #188-D: enumerated type mixed with another type
  	SSD1306_Puts("Click B: Run BWD",&Font_7x10,0x01);
../Core/Src/main.c(628): warning:  #188-D: enumerated type mixed with another type
  	SSD1306_Puts("Click C: Stop/Back",&Font_7x10,0x01);
../Core/Src/main.c(630): warning:  #188-D: enumerated type mixed with another type
  	SSD1306_Puts("Click D: Open Menu",&Font_7x10,0x01);
../Core/Src/main.c(636): warning:  #188-D: enumerated type mixed with another type
  	SSD1306_Puts("COF Measurament",&Font_7x10,0x01);
../Core/Src/main.c(638): warning:  #188-D: enumerated type mixed with another type
  	SSD1306_Puts("--------------------",&Font_7x10,0x01);
../Core/Src/main.c(640): warning:  #188-D: enumerated type mixed with another type
  	SSD1306_Puts("Click A: Set_Home",&Font_7x10,0x01);
../Core/Src/main.c(642): warning:  #188-D: enumerated type mixed with another type
  	SSD1306_Puts("Click B: Run COF",&Font_7x10,0x01);
../Core/Src/main.c(644): warning:  #188-D: enumerated type mixed with another type
  	SSD1306_Puts("Click C: Back",&Font_7x10,0x01);
../Core/Src/main.c(646): warning:  #188-D: enumerated type mixed with another type
  	SSD1306_Puts("Click D: COF_Setup",&Font_7x10,0x01);
../Core/Src/main.c(653): warning:  #188-D: enumerated type mixed with another type
  	SSD1306_Puts("COF Measurament",&Font_7x10,0x01);
../Core/Src/main.c(655): warning:  #188-D: enumerated type mixed with another type
  	SSD1306_Puts("--------------------",&Font_7x10,0x01);
../Core/Src/main.c(668): warning:  #188-D: enumerated type mixed with another type
  	SSD1306_Puts("S.F= ",&Font_11x18,0x01);
../Core/Src/main.c(671): warning:  #188-D: enumerated type mixed with another type
  	SSD1306_Puts(V ,&Font_11x18,0x01);
../Core/Src/main.c(673): warning:  #188-D: enumerated type mixed with another type
  	SSD1306_Puts(".",&Font_11x18,0x01);
../Core/Src/main.c(678): warning:  #188-D: enumerated type mixed with another type
  		SSD1306_Puts(R ,&Font_11x18,0x01);
../Core/Src/main.c(683): warning:  #188-D: enumerated type mixed with another type
  		SSD1306_Puts("0",&Font_11x18,0x01);
../Core/Src/main.c(686): warning:  #188-D: enumerated type mixed with another type
  		SSD1306_Puts(R ,&Font_11x18,0x01);
../Core/Src/main.c(691): warning:  #188-D: enumerated type mixed with another type
  		SSD1306_Puts("00",&Font_11x18,0x01);
../Core/Src/main.c(694): warning:  #188-D: enumerated type mixed with another type
  		SSD1306_Puts(R ,&Font_11x18,0x01);
../Core/Src/main.c(698): warning:  #188-D: enumerated type mixed with another type
  	SSD1306_Puts("K.F= ",&Font_11x18,0x01);
../Core/Src/main.c(701): warning:  #188-D: enumerated type mixed with another type
  	SSD1306_Puts(V ,&Font_11x18,0x01);
../Core/Src/main.c(703): warning:  #188-D: enumerated type mixed with another type
  	SSD1306_Puts(".",&Font_11x18,0x01);
../Core/Src/main.c(708): warning:  #188-D: enumerated type mixed with another type
  		SSD1306_Puts(R ,&Font_11x18,0x01);
../Core/Src/main.c(713): warning:  #188-D: enumerated type mixed with another type
  		SSD1306_Puts("0" ,&Font_11x18,0x01);
../Core/Src/main.c(716): warning:  #188-D: enumerated type mixed with another type
  		SSD1306_Puts(R ,&Font_11x18,0x01);
../Core/Src/main.c(721): warning:  #188-D: enumerated type mixed with another type
  		SSD1306_Puts("00" ,&Font_11x18,0x01);
../Core/Src/main.c(724): warning:  #188-D: enumerated type mixed with another type
  		SSD1306_Puts(R ,&Font_11x18,0x01);
../Core/Src/main.c(735): warning:  #188-D: enumerated type mixed with another type
  	SSD1306_Puts("COF Measurament",&Font_7x10,0x01);
../Core/Src/main.c(737): warning:  #188-D: enumerated type mixed with another type
  	SSD1306_Puts("--------------------",&Font_7x10,0x01);
../Core/Src/main.c(741): warning:  #188-D: enumerated type mixed with another type
  	SSD1306_Puts("SETTING",&Font_11x18,0x01);
../Core/Src/main.c(743): warning:  #188-D: enumerated type mixed with another type
  	SSD1306_Puts("HOME...",&Font_11x18,0x01);
../Core/Src/main.c(749): warning:  #188-D: enumerated type mixed with another type
  	SSD1306_Puts("COF Measurament",&Font_7x10,0x01);
../Core/Src/main.c(751): warning:  #188-D: enumerated type mixed with another type
  	SSD1306_Puts("--------------------",&Font_7x10,0x01);
../Core/Src/main.c(756): warning:  #188-D: enumerated type mixed with another type
  		SSD1306_Puts("SetHOME",&Font_11x18,0x01);
../Core/Src/main.c(758): warning:  #188-D: enumerated type mixed with another type
  		SSD1306_Puts("First",&Font_11x18,0x01);
../Core/Src/main.c(762): warning:  #188-D: enumerated type mixed with another type
  		SSD1306_Puts("                         ",&Font_11x18,0x01);
../Core/Src/main.c(764): warning:  #188-D: enumerated type mixed with another type
  		SSD1306_Puts("                        ",&Font_11x18,0x01);
../Core/Src/main.c(776): warning:  #188-D: enumerated type mixed with another type
  	SSD1306_Puts("COF Measurament",&Font_7x10,0x01);
../Core/Src/main.c(778): warning:  #188-D: enumerated type mixed with another type
  	SSD1306_Puts("--------------------",&Font_7x10,0x01);
../Core/Src/main.c(783): warning:  #188-D: enumerated type mixed with another type
  		SSD1306_Puts("You Are",&Font_11x18,0x01);
../Core/Src/main.c(785): warning:  #188-D: enumerated type mixed with another type
  		SSD1306_Puts("At Home",&Font_11x18,0x01);
../Core/Src/main.c(789): warning:  #188-D: enumerated type mixed with another type
  		SSD1306_Puts("                         ",&Font_11x18,0x01);
../Core/Src/main.c(791): warning:  #188-D: enumerated type mixed with another type
  		SSD1306_Puts("                        ",&Font_11x18,0x01);
../Core/Src/main.c(800): warning:  #188-D: enumerated type mixed with another type
  	SSD1306_Puts("COF SETTING",&Font_7x10,0x01);
../Core/Src/main.c(802): warning:  #188-D: enumerated type mixed with another type
  	SSD1306_Puts("--------------------",&Font_7x10,0x01);
../Core/Src/main.c(804): warning:  #188-D: enumerated type mixed with another type
  	SSD1306_Puts("Change COF Speed",&Font_7x10,Change_COF_Speed);
../Core/Src/main.c(806): warning:  #188-D: enumerated type mixed with another type
  	SSD1306_Puts("Change Distance",&Font_7x10,Change_COF_Distance);
../Core/Src/main.c(808): warning:  #188-D: enumerated type mixed with another type
  	SSD1306_Puts("Set Zero",&Font_7x10,Set_Zero);
../Core/Src/main.c(819): warning:  #188-D: enumerated type mixed with another type
  	SSD1306_Puts("SET ZERO",&Font_7x10,0x01);
../Core/Src/main.c(821): warning:  #188-D: enumerated type mixed with another type
  	SSD1306_Puts("--------------------",&Font_7x10,0x01);
../Core/Src/main.c(824): warning:  #188-D: enumerated type mixed with another type
  	SSD1306_Puts("Make sure pull",&Font_7x10,0x01);
../Core/Src/main.c(826): warning:  #188-D: enumerated type mixed with another type
  	SSD1306_Puts("Cable is loose",&Font_7x10,0x01);
../Core/Src/main.c(829): warning:  #188-D: enumerated type mixed with another type
  	SSD1306_Puts("D:Yes",&Font_7x10,0x01);
../Core/Src/main.c(831): warning:  #188-D: enumerated type mixed with another type
  	SSD1306_Puts("C:Back",&Font_7x10,0x01);
../Core/Src/main.c(837): warning:  #188-D: enumerated type mixed with another type
  	SSD1306_Puts("NOTIFICATION",&Font_7x10,0x01);
../Core/Src/main.c(839): warning:  #188-D: enumerated type mixed with another type
  	SSD1306_Puts("--------------------",&Font_7x10,0x01);
../Core/Src/main.c(842): warning:  #188-D: enumerated type mixed with another type
  	SSD1306_Puts("Successful",&Font_7x10,0x01);
../Core/Src/main.c(846): warning:  #188-D: enumerated type mixed with another type
  	SSD1306_Puts("Restarting",&Font_7x10,0x01);
../Core/Src/main.c(850): warning:  #188-D: enumerated type mixed with another type
  	SSD1306_Puts("",&Font_7x10,0x01);
../Core/Src/main.c(854): warning:  #188-D: enumerated type mixed with another type
  	SSD1306_Puts(".",&Font_7x10,0x01);
../Core/Src/main.c(858): warning:  #188-D: enumerated type mixed with another type
  	SSD1306_Puts("..",&Font_7x10,0x01);
../Core/Src/main.c(862): warning:  #188-D: enumerated type mixed with another type
  	SSD1306_Puts("...",&Font_7x10,0x01);
../Core/Src/main.c(866): warning:  #188-D: enumerated type mixed with another type
  	SSD1306_Puts("....",&Font_7x10,0x01);
../Core/Src/main.c(870): warning:  #188-D: enumerated type mixed with another type
  	SSD1306_Puts(".....",&Font_7x10,0x01);
../Core/Src/main.c(874): warning:  #188-D: enumerated type mixed with another type
  	SSD1306_Puts("......",&Font_7x10,0x01);
../Core/Src/main.c(878): warning:  #188-D: enumerated type mixed with another type
  	SSD1306_Puts(".......",&Font_7x10,0x01);
../Core/Src/main.c(882): warning:  #188-D: enumerated type mixed with another type
  	SSD1306_Puts("........",&Font_7x10,0x01);
../Core/Src/main.c(886): warning:  #188-D: enumerated type mixed with another type
  	SSD1306_Puts(".........",&Font_7x10,0x01);
../Core/Src/main.c(890): warning:  #188-D: enumerated type mixed with another type
  	SSD1306_Puts("..........",&Font_7x10,0x01);
../Core/Src/main.c(898): warning:  #188-D: enumerated type mixed with another type
  	SSD1306_Puts("COF SPEED",&Font_7x10,0x01);
../Core/Src/main.c(900): warning:  #188-D: enumerated type mixed with another type
  	SSD1306_Puts("--------------------",&Font_7x10,0x01);
../Core/Src/main.c(902): warning:  #188-D: enumerated type mixed with another type
  	SSD1306_Puts("V=",&Font_11x18,0x01);
../Core/Src/main.c(908): warning:  #188-D: enumerated type mixed with another type
  	SSD1306_Puts(V ,&Font_11x18,0x01);
../Core/Src/main.c(910): warning:  #188-D: enumerated type mixed with another type
  	SSD1306_Puts(".",&Font_11x18,0x01);
../Core/Src/main.c(913): warning:  #188-D: enumerated type mixed with another type
  	SSD1306_Puts(R ,&Font_11x18,0x01);
../Core/Src/main.c(915): warning:  #188-D: enumerated type mixed with another type
  	SSD1306_Puts("m/min",&Font_7x10,0x01);
../Core/Src/main.c(926): warning:  #188-D: enumerated type mixed with another type
  	SSD1306_Puts("a",&Font_7x10,0x00);
../Core/Src/main.c(928): warning:  #188-D: enumerated type mixed with another type
  	SSD1306_Puts(":Up",&Font_7x10,0x01);
../Core/Src/main.c(931): warning:  #188-D: enumerated type mixed with another type
  	SSD1306_Puts("b",&Font_7x10,0x00);
../Core/Src/main.c(933): warning:  #188-D: enumerated type mixed with another type
  	SSD1306_Puts(":DWN",&Font_7x10,0x01);
../Core/Src/main.c(936): warning:  #188-D: enumerated type mixed with another type
  	SSD1306_Puts("c",&Font_7x10,0x00);
../Core/Src/main.c(938): warning:  #188-D: enumerated type mixed with another type
  	SSD1306_Puts(":<",&Font_7x10,0x01);
../Core/Src/main.c(941): warning:  #188-D: enumerated type mixed with another type
  	SSD1306_Puts("d",&Font_7x10,0x00);
../Core/Src/main.c(943): warning:  #188-D: enumerated type mixed with another type
  	SSD1306_Puts(":Ent",&Font_7x10,0x01);
../Core/Src/main.c(950): warning:  #188-D: enumerated type mixed with another type
  	SSD1306_Puts("COF DISTANCE",&Font_7x10,0x01);
../Core/Src/main.c(952): warning:  #188-D: enumerated type mixed with another type
  	SSD1306_Puts("--------------------",&Font_7x10,0x01);
../Core/Src/main.c(954): warning:  #188-D: enumerated type mixed with another type
  	SSD1306_Puts("S=",&Font_11x18,0x01);
../Core/Src/main.c(960): warning:  #188-D: enumerated type mixed with another type
  	SSD1306_Puts(COF_Dis ,&Font_11x18,0x01);
../Core/Src/main.c(963): warning:  #188-D: enumerated type mixed with another type
  	SSD1306_Puts("mm",&Font_7x10,0x01);
../Core/Src/main.c(966): warning:  #188-D: enumerated type mixed with another type
  	SSD1306_Puts("a",&Font_7x10,0x00);
../Core/Src/main.c(968): warning:  #188-D: enumerated type mixed with another type
  	SSD1306_Puts(":Up",&Font_7x10,0x01);
../Core/Src/main.c(971): warning:  #188-D: enumerated type mixed with another type
  	SSD1306_Puts("b",&Font_7x10,0x00);
../Core/Src/main.c(973): warning:  #188-D: enumerated type mixed with another type
  	SSD1306_Puts(":DWN",&Font_7x10,0x01);
../Core/Src/main.c(976): warning:  #188-D: enumerated type mixed with another type
  	SSD1306_Puts("c",&Font_7x10,0x00);
../Core/Src/main.c(978): warning:  #188-D: enumerated type mixed with another type
  	SSD1306_Puts(":<",&Font_7x10,0x01);
../Core/Src/main.c(981): warning:  #188-D: enumerated type mixed with another type
  	SSD1306_Puts("d",&Font_7x10,0x00);
../Core/Src/main.c(983): warning:  #188-D: enumerated type mixed with another type
  	SSD1306_Puts(":Ent",&Font_7x10,0x01);
../Core/Src/main.c(2079): warning:  #188-D: enumerated type mixed with another type
  	SSD1306_Puts("Formulating",&Font_7x10,0x01);
../Core/Src/main.c(2081): warning:  #188-D: enumerated type mixed with another type
  	SSD1306_Puts("A Greener World",&Font_7x10,0x01);
../Core/Src/main.c: 143 warnings, 0 errors
linking...
Program Size: Code=46848 RO-data=7048 RW-data=720 ZI-data=17976  
FromELF: creating hex file...
"Menu\Menu.axf" - 0 Error(s), 143 Warning(s).

Software Packages used:

Package Vendor: ARM
                http://www.keil.com/pack/ARM.CMSIS.5.7.0.pack
                ARM.CMSIS.5.7.0
                CMSIS (Cortex Microcontroller Software Interface Standard)
   * Component: CORE Version: 5.4.0

Package Vendor: Keil
                http://www.keil.com/pack/Keil.STM32F1xx_DFP.2.4.0.pack
                Keil.STM32F1xx_DFP.2.4.0
                STMicroelectronics STM32F1 Series Device Support, Drivers and Examples

Collection of Component include folders:

  .\RTE\_Menu
  C:\Users\democ\AppData\Local\Arm\Packs\ARM\CMSIS\5.7.0\CMSIS\Core\Include
  C:\Users\democ\AppData\Local\Arm\Packs\Keil\STM32F1xx_DFP\2.4.0\Device\Include

Collection of Component Files used:

   * Component: ARM::CMSIS:CORE:5.4.0
Build Time Elapsed:  00:00:01

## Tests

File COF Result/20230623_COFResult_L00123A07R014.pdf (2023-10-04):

# MYLAN GROUP

## Longduc Industrial Park Travinh City, Travinh Province, Vietnam Tel : +84 294 3846 997 – ext: 3501 Fax: +84 294 3846 998

### OPERATOR: DATE:

### COF SPEED: COF DISTANCE: TEMPERATURE: HUMIDITY: COF METHOD:

## 150 mm/min

130 mm
26
10
1
NO. | SAMPLE | NOTE | LoT | SF | KF | Std_Dev | TIME
COF1 | BOPET//PE | X2, VSled | L00123A07R014 | 0.741 | 0.611 | 3.15 | 23-06-23 10:42:00
COF2 | BOPET//PE | X2, HSled | L00123A07R014 | 0.675 | 0.533 | 2.56 | 23-06-23 10:48:46
COF3 | BOPET//PE | X2, VSled 2 | L00123A07R014 | 0.639 | 0.633 | 3.24 | 23-06-23 10:50:42
COF4 | BOPET//PE | X2, VSled 3 | L00123A07R014 | 0.721 | 0.625 | 3.89 | 23-06-23 10:52:02
COF5 | BOPET//PE | X2, HSled 2 | L00123A07R014 | 0.605 | 0.534 | 1.54 | 23-06-23 10:53:43
COF6 | BOPET//PE | X2, HSled 3 | L00123A07R014 | 0.611 | 0.547 | 3.04 | 23-06-23 10:54:54

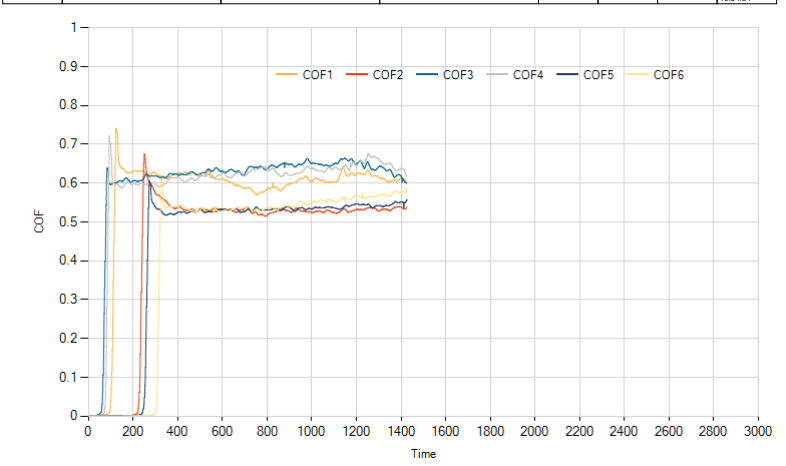
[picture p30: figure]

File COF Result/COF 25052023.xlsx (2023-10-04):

TỔNG HỢP KẾT QUẢ ĐO COF, MỨC NLBM VÀ GÓC TIẾP XÚC CỦA CÁC MẪU MÀNG GHÉP ĐÃ CORONA
STT | Cấu trúc | Điều kiện corona | Lot | COF |  | NLBM |  |  | Góc tiếp xúc
 |  |  |  | sF | kF | L1 | L2 | L3
1 |  | XL 3L | L00423C15R013 | 0.651 | 0.642
2 |  | XL 2L | L00123A17R011 | 0.809 | 0.71
3 |  | XL 1L | L00423C15R013 | 0.586 | 0.592
4 |  | XL 3L | L00323B20R006 | 0.556 | 0.556
5 |  | XL 3L | L00723E16R004 | 0.679 | 0.622
6 |  | XL 0L | L00723E16R004 | 0.11 | 0.107
7 |  | XL 0L | L00426C15R013 | 0.256 | 0.269
8
9
10
11
12
13

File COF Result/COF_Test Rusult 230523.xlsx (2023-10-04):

Test COF trên cùng mẫu đo
 | 1 | 2 | 3 | 4 | 5 | 6 | 7 | 8 | 9 | 10 | 11 | 12 | 13 | 14 | 15 | 16 | 17 | 18 | 19 | 20 | 21 | 22 | 23
SF | 0.291 | 0.29 | 0.294 | 0.293 | 0.294 | 0.295 | 0.287 | 0.278 | 0.283 | 0.286 | 0.287 | 0.292 | 0.283 | 0.3 | 0.293 | 0.301 | 0.278 | 0.29 | 0.301 | 0.283 | 0.279 | 0.281 | 0.28
KF | 0.283 | 0.285 | 0.284 | 0.284 | 0.282 | 0.286 | 0.285 | 0.283 | 0.28 | 0.284 | 0.282 | 0.28 | 0.276 | 0.283 | 0.282 | 0.281 | 0.273 | 0.274 | 0.277 | 0.275 | 0.275 | 0.276 | 0.269
Sai số so với dữ liệu đầu tiên
 |  | -0.3436426117 | 1.030927835 | 0.6872852234 | 1.030927835 | 1.374570447 | -1.374570447 | -4.467353952 | -2.749140893 | -1.718213058 | -1.374570447 | 0.3436426117 | -2.749140893 | 3.092783505 | 0.6872852234 | 3.436426117 | -4.467353952 | -0.3436426117 | 3.436426117 | -2.749140893 | -4.12371134 | -3.436426117 | -3.780068729
 |  | 0.7067137809 | 0.3533568905 | 0.3533568905 | -0.3533568905 | 1.060070671 | 0.7067137809 | 0 | -1.060070671 | 0.3533568905 | -0.3533568905 | -1.060070671 | -2.473498233 | 0 | -0.3533568905 | -0.7067137809 | -3.533568905 | -3.180212014 | -2.120141343 | -2.826855124 | -2.826855124 | -2.473498233 | -4.946996466

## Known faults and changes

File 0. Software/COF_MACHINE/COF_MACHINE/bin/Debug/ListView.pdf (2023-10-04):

NO. | SAMPL E | NOTE | LoT | SF | KF | Std_De v | USER | TIME
COF1 | aaaaaa aaa | aaaaaa aaaa | aaaaaa aaaaa | 0 | 0 | 0 | aaaaaa aaaaa | 6/15/20 23

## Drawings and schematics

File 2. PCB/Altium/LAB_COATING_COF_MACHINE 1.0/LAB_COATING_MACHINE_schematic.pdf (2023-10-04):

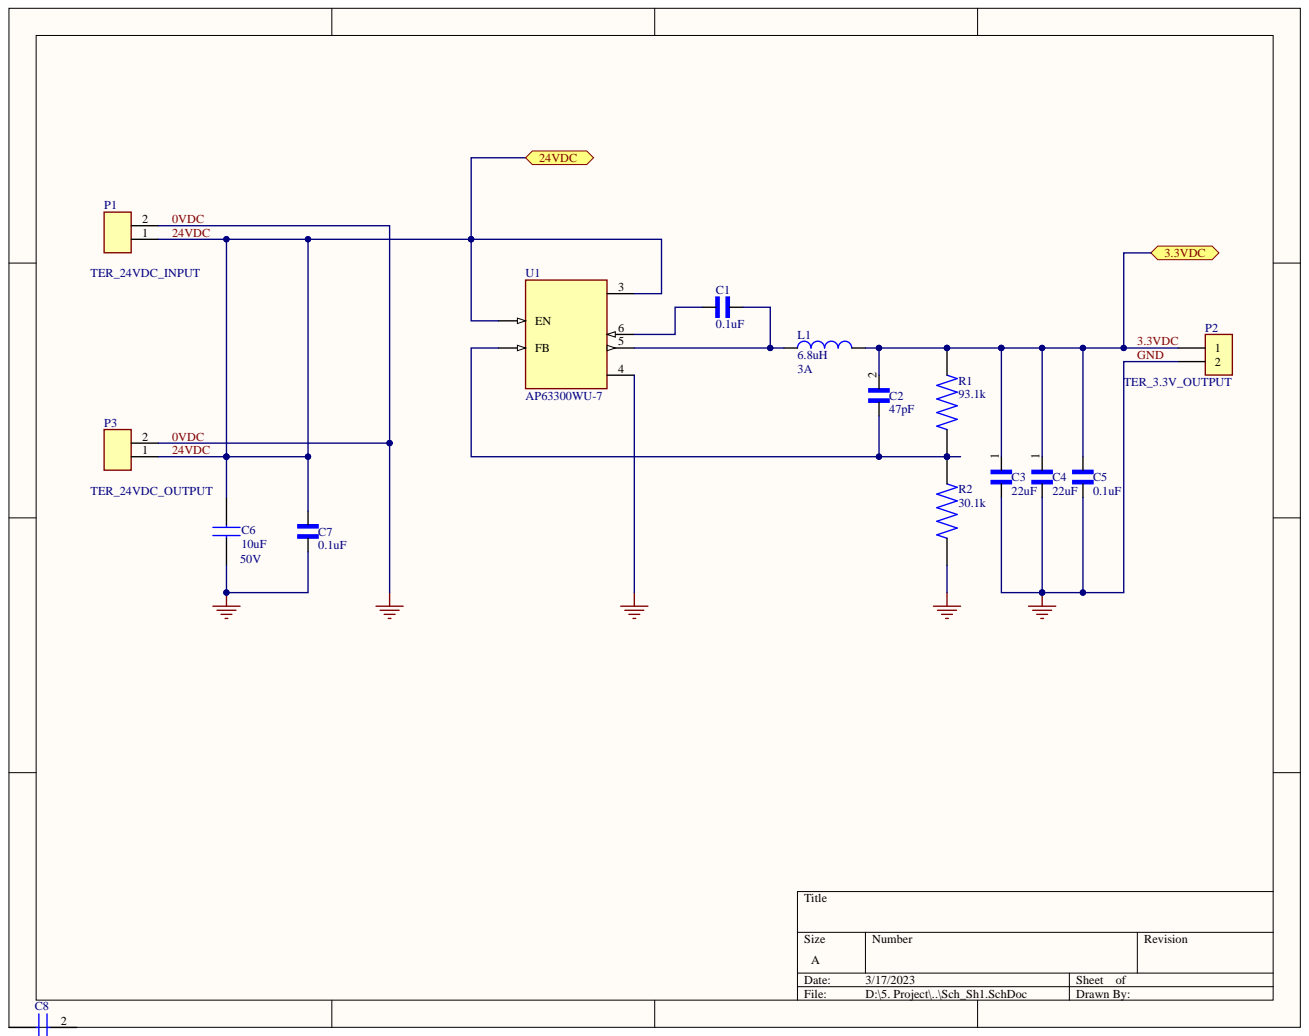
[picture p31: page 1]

24VDC

0VDC | | U1

24VDC | | C7

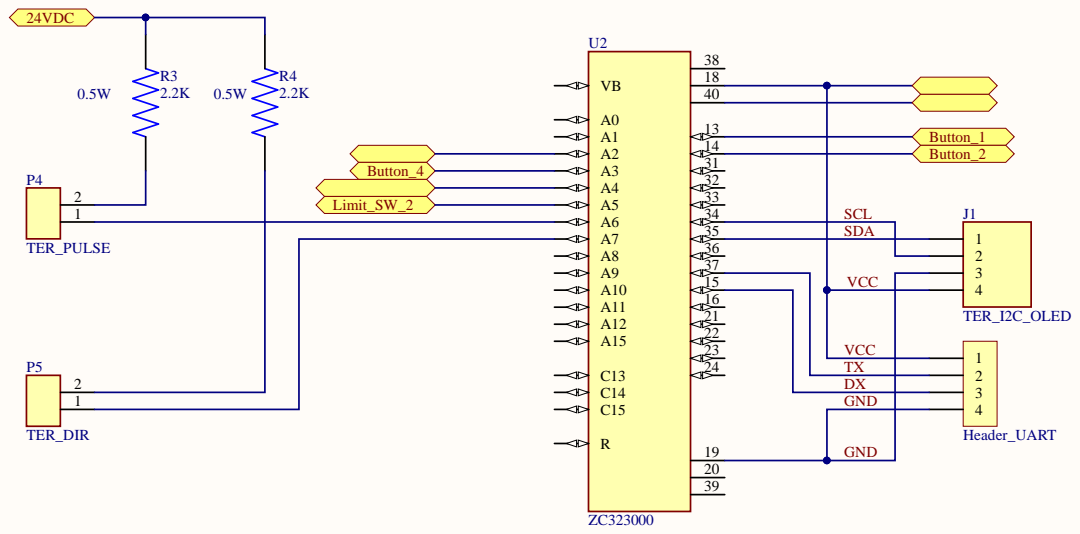
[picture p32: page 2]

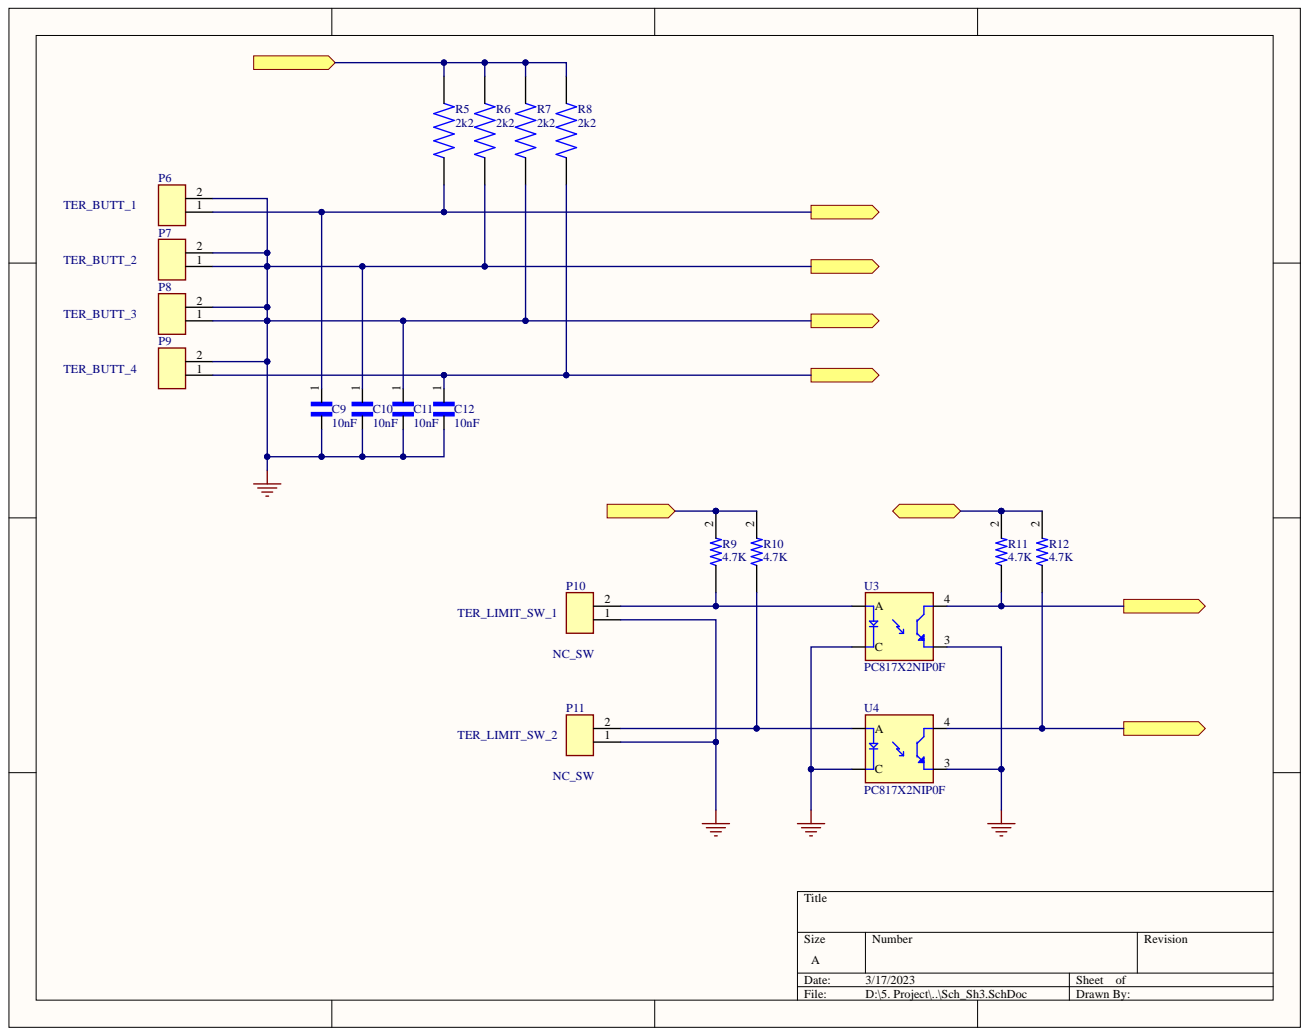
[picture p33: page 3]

# Board S

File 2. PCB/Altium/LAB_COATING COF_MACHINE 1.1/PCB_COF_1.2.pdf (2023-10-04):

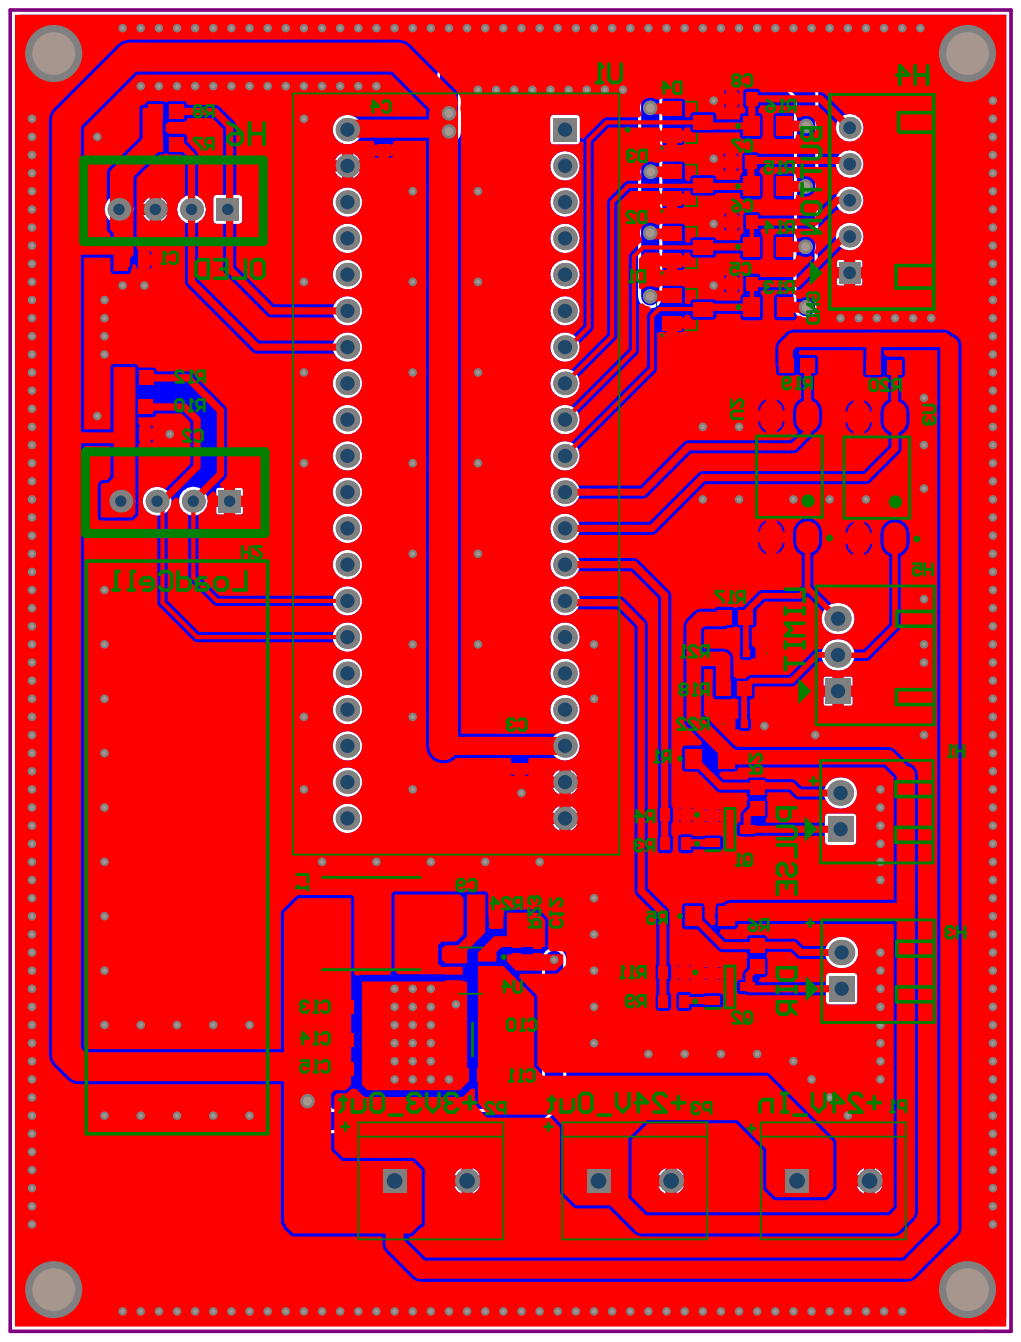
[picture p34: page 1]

Component list | <Parameter Title not found>
Source Data From: | | LAB_COATING COF_MACHINE.PrjPcb
Project: | | LAB_COATING COF_MACHINE.PrjPcb
Variant: | | None
Report Date: | 5/9/2023 | 8:14:14 AM
Print Date: | 09-May-23 | 8:14:19 AM
# | Designator | LibRef #Column Name Error:Manufact | | Description | Footprint | #Column Name Error:Library Name | Comment | Quantity

1 | C1, C2, C3, C4, C13, C14 | CAP CER 22UF 6.3V X5R 0603 -GRM188R60J226MEA0D | | CAP CER 22UF 6.3V X5R 0603 | C 0603 | | 22uF | 6
2 | C5, C6, C7, C8, C15 | CAP CER 0.1UF 10V X7R 0603 -C0603C104K8RACTU | | Multilayer Ceramic Capacitors MLCC -SMD/SMT | CAPC1608X95N | | 0.1uF | 5
3 | C9, C11 | CAP CER 0.1UF 50V X7R 0603 - ESD35C104K4T2A-24 | | CAP CER 0.1UF 50V X7R 0603 | C 0603 | | 0.1uF | 2
4 | C10 | CAP CER 10UF 50V Y5V 1210 - 12105G106ZAT2A | | CAP CER 10UF 50V Y5V 1210 | CAPC3225X290N | | 10uF | 1
5 | C12 | CAP CER 56PF 50V C0G/NPO 0402 -CC0402JRNPO9BN560 | | CAP CER 56PF 50V C0G/NPO 0402 | CAPC1005X55N | | 56pF | 1
6 | D1, D2, D3, D4 | DIODE SCHOTTKY 30V 150MA SOT23 - BAT54S | | DIODE SCHOTTKY 30V 150MA SOT23 | SOT95P240X120-3N | | BAT54S | 4
7 | H1, H3 | Header 2P 2.54 Duc Cong | | Cắm | Header 2P DC 2.54 | | Pulse | 2
8 | H2, H6 | Header 4P 2.54 Duc Thang | | Cắm | XH2.54M-4 | | HEADER_UART_MODULE | 2
9 | H4 | Header 5P 2.54 Duc Cong | | Cắm | Header 5P DC 2.54 | | Button_1-4 | 1
10 | H5 | Header 3P 2.54 Duc Cong | | Cắm | Header 3P DC 2.54 | | Limit_SW_1-2 | 1
11 | L1 | IND 4.7UH 5.5A 40 MOHM SMD -IHLP2525CZER4R7M01 | | FIXED IND 4.7UH 5.5A 40 MOHM SMD | INDM6965X300N | | 4.7uF | 1
12 | P1 | TERM BLK 2P SIDE ENT 5.08MM PCB - 282837-2 | | TERM BLK 2P SIDE ENT 5.08MM PCB | TE_282837-2 | | TERM BLK 2P SIDE ENT 5.08MM PCB -282837-2 | 1
13 | P2, P3 | 282837-2 | | Connector Terminal Blocks Receptacle 2 Position 5.08mm Solder Straight Thru-Hole 13.5A/Contact | TE_282837-2 | | 282837-2 | 2
14 | Q1, Q2 | TRANS NPN 45V 0.8A SOT23-3 - BCW66GLT1G | | TRANS NPN 45V 0.8A SOT23-3 | SOT95P237X111-3N | | TRANS NPN 45V 0.8A SOT23-3 -BCW66GLT1G | 2
15 | R1, R5, R13, R14, R15, R16 | RES SMD 2.2K OHM 5% 1/2W 0805 - ERJ-P06J222V | | RES SMD 2.2K OHM 5% 1/2W 0805 | RES 0805 | | 2.2K | 6
16 | R2, R6 | RES SMD 100K OHM 1% 1/10W 0603 -CRCW0603100KFKEA | | RES SMD 100K OHM 1% 1/10W 0603 | Res 0603 | | 100K | 2
17 | R3, R9 | RES SMD 1K OHM 5% 1/10W 0603 - ERJ-3GEYJ102V | | RES SMD 1K OHM 5% 1/10W 0603 | ERJ3EKF1000V | | 1K | 2
18 | R4, R11 | RES SMD 10K OHM 5% 1/10W 0603 -ERJ3GEYJ103V | | RES SMD 10K OHM 5% 1/10W 0603 | ERJ3EKF1000V | | 10K | 2
19 | R7, R8, R10, R12, R19, R20 | RES 4.7K OHM 1% 1/10W 0603 - RC0603FR-074K7L | | RES 4.7K OHM 1% 1/10W 0603 | Res 0603 | | 4.7k | 6
20 | R17, R18 | RES SMD 9.1K OHM 1% 1/10W 0603 - ERJ-3EKF9101V | | RES SMD 9.1K OHM 1% 1/10W 0603 | Res 0603 | | 9k1 | 2
21 | R21, R22 | RES SMD 100K OHM 1% 1/10W 0402 -ERJ2RKF1003X | | RES SMD 100K OHM 1% 1/10W 0402 | ERJ2RKD1004X | | 100k | 2
22 | R23 | RES 93.1K OHM 1% 1/16W 0402 - RC0402FR-0793K1L | | RES 93.1K OHM 1% 1/16W 0402 | RESC1005X40N | | 93.1k | 1
23 | R24 | RES SMD 30.1K OHM 1% 1/10W 0402 - ERJ-2RKF3012X | | RES SMD 30.1K OHM 1% 1/10W 0402 | ERJ2RKD1004X | | 30.1k | 1
24 | U1 | MODULE STM32F103C8T6 -ZC323000 | | MODULE STM32F103C8T6 | MODULE_ZC323000 | | MODULE STM32F103C8T6 - ZC323000 | 1
25 | U2, U3 | OPTOISOLATOR 5KV TRANS 4SMD -PC817X2NIP0F | | Optoisolator Transistor Output 5000Vrms 1 Channel 4-SMD | SOT254P975X400-4N | | OPTOISOLATOR 5KV TRANS 4SMD -PC817X2NIP0F | 2
26 | U4 | IC REG BUCK ADJUSTABLE 2A TSOT26 - AP63300WU-7 | | IC REG BUCK ADJUSTABLE 2A TSOT26 | SOT95P280X100-6N | | IC REG BUCK ADJUSTABLE 2A TSOT26 -AP63300WU-7 | 1
Approved | | | Notes | | | | | 59

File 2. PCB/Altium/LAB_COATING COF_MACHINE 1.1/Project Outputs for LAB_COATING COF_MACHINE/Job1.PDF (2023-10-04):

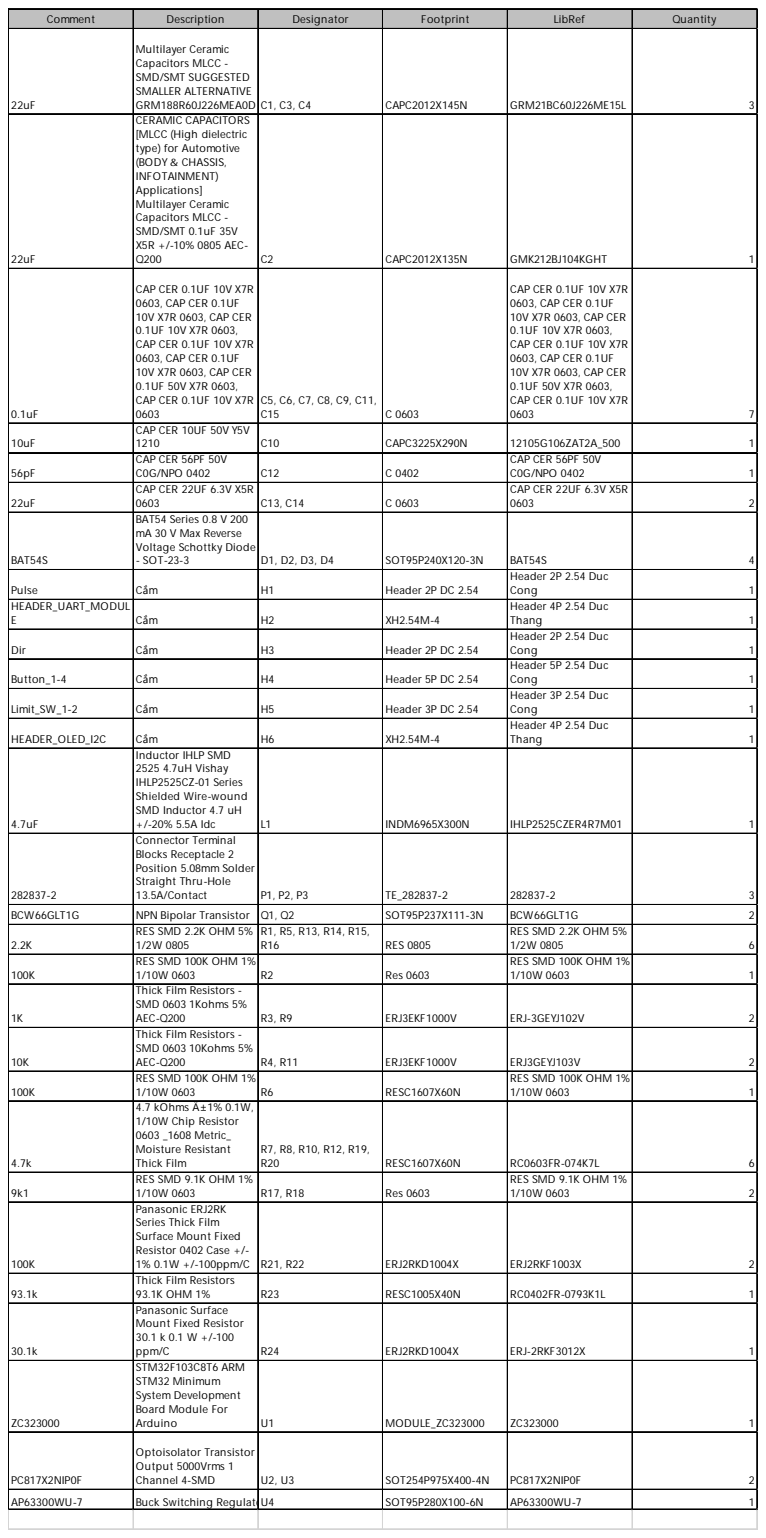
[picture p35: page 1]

Comment | Description | Designator | Footprint | LibRef | Quantity

22uF | Multilayer Ceramic Capacitors MLCC -SMD/SMT SUGGESTED SMALLER ALTERNATIVE GRM188R60J226MEA0D | C1, C3, C4 | CAPC2012X145N | GRM21BC60J226ME15L | 3

22uF | CERAMIC CAPACITORS [MLCC (High dielectric type) for Automotive (BODY & CHASSIS, INFOTAINMENT) Applications] Multilayer Ceramic Capacitors MLCC -SMD/SMT 0.1uF 35V X5R +/-10% 0805 AEC-Q200 | C2 | CAPC2012X135N | GMK212BJ104KGHT | 1

0.1uF | CAP CER 0.1UF 10V X7R 0603, CAP CER 0.1UF 10V X7R 0603, CAP CER 0.1UF 10V X7R 0603, CAP CER 0.1UF 10V X7R 0603, CAP CER 0.1UF 10V X7R 0603, CAP CER 0.1UF 50V X7R 0603, CAP CER 0.1UF 10V X7R 0603 | C5, C6, C7, C8, C9, C11, C15 | C 0603 | CAP CER 0.1UF 10V X7R 0603, CAP CER 0.1UF 10V X7R 0603, CAP CER 0.1UF 10V X7R 0603, CAP CER 0.1UF 10V X7R 0603, CAP CER 0.1UF 10V X7R 0603, CAP CER 0.1UF 50V X7R 0603, CAP CER 0.1UF 10V X7R 0603 | 7

10uF | CAP CER 10UF 50V Y5V 1210 | C10 | CAPC3225X290N | 12105G106ZAT2A_500 | 1

56pF | CAP CER 56PF 50V C0G/NPO 0402 | C12 | C 0402 | CAP CER 56PF 50V C0G/NPO 0402 | 1

22uF | CAP CER 22UF 6.3V X5R 0603 | C13, C14 | C 0603 | CAP CER 22UF 6.3V X5R 0603 | 2

BAT54S | BAT54 Series 0.8 V 200 mA 30 V Max Reverse Voltage Schottky Diode - SOT-23-3 | D1, D2, D3, D4 | SOT95P240X120-3N | BAT54S | 4

Pulse | Cắm | H1 | Header 2P DC 2.54 | Header 2P 2.54 Duc Cong | 1

HEADER_UART_MODUL E | Cắm | H2 | XH2.54M-4 | Header 4P 2.54 Duc Thang | 1

Dir | Cắm | H3 | Header 2P DC 2.54 | Header 2P 2.54 Duc Cong | 1

Button_1-4 | Cắm | H4 | Header 5P DC 2.54 | Header 5P 2.54 Duc Cong | 1

Limit_SW_1-2 | Cắm | H5 | Header 3P DC 2.54 | Header 3P 2.54 Duc Cong | 1

HEADER_OLED_I2C | Cắm | H6 | XH2.54M-4 | Header 4P 2.54 Duc Thang | 1

4.7uF | Inductor IHLP SMD 2525 4.7uH Vishay IHLP2525CZ-01 Series Shielded Wire-wound SMD Inductor 4.7 uH +/-20% 5.5A Idc | L1 | INDM6965X300N | IHLP2525CZER4R7M01 | 1

282837-2 | Connector Terminal Blocks Receptacle 2 Position 5.08mm Solder Straight Thru-Hole 13.5A/Contact | P1, P2, P3 | TE_282837-2 | 282837-2 | 3

BCW66GLT1G | NPN Bipolar Transistor | Q1, Q2 | SOT95P237X111-3N | BCW66GLT1G | 2
2.2K | RES SMD 2.2K OHM 5% 1/2W 0805 | R1, R5, R13, R14, R15, R16 | RES 0805 | RES SMD 2.2K OHM 5% 1/2W 0805 | 6

100K | RES SMD 100K OHM 1% 1/10W 0603 | R2 | Res 0603 | RES SMD 100K OHM 1% 1/10W 0603 | 1

1K | Thick Film Resistors -SMD 0603 1Kohms 5% AEC-Q200 | R3, R9 | ERJ3EKF1000V | ERJ-3GEYJ102V | 2

10K | Thick Film Resistors -SMD 0603 10Kohms 5% AEC-Q200 | R4, R11 | ERJ3EKF1000V | ERJ3GEYJ103V | 2

100K | RES SMD 100K OHM 1% 1/10W 0603 | R6 | RESC1607X60N | RES SMD 100K OHM 1% 1/10W 0603 | 1

4.7k | 4.7 kOhms Â±1% 0.1W, 1/10W Chip Resistor 0603 _1608 Metric_ Moisture Resistant Thick Film | R7, R8, R10, R12, R19, R20 | RESC1607X60N | RC0603FR-074K7L | 6

9k1 | RES SMD 9.1K OHM 1% 1/10W 0603 | R17, R18 | Res 0603 | RES SMD 9.1K OHM 1% 1/10W 0603 | 2

100K | Panasonic ERJ2RK Series Thick Film Surface Mount Fixed Resistor 0402 Case +/-1% 0.1W +/-100ppm/C | R21, R22 | ERJ2RKD1004X | ERJ2RKF1003X | 2

93.1k | Thick Film Resistors 93.1K OHM 1% | R23 | RESC1005X40N | RC0402FR-0793K1L | 1

30.1k | Panasonic Surface Mount Fixed Resistor 30.1 k 0.1 W +/-100 ppm/C | R24 | ERJ2RKD1004X | ERJ-2RKF3012X | 1

ZC323000 | STM32F103C8T6 ARM STM32 Minimum System Development Board Module For Arduino | U1 | MODULE_ZC323000 | ZC323000 | 1

PC817X2NIP0F | Optoisolator Transistor Output 5000Vrms 1 Channel 4-SMD | U2, U3 | SOT254P975X400-4N | PC817X2NIP0F | 2

AP63300WU-7 | Buck Switching RegulatoU 4 | | SOT 95P280X 100- 6N | AP 63300W U-7 | 1

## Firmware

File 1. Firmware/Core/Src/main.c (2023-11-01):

/* USER CODE BEGIN Header */
/**
  ******************************************************************************
  * @file           : main.c
  * @brief          : Main program body
  ******************************************************************************
  * @attention
  *
  * Copyright (c) 2023 STMicroelectronics.
  * All rights reserved.
  *
  * This software is licensed under terms that can be found in the LICENSE file
  * in the root directory of this software component.
  * If no LICENSE file comes with this software, it is provided AS-IS.
  *
  ******************************************************************************
  */
/* USER CODE END Header */
/* Includes ------------------------------------------------------------------*/
#include "main.h"
#include "usb_device.h"

/* Private includes ----------------------------------------------------------*/
/* USER CODE BEGIN Includes */
#include "math.h"
#include "ssd1306.h"
#include "fonts.h"
#include "mylan.h"
#include "modbus_crc.h"
#include "string.h"
#include "usbd_cdc_if.h"

#define FLASH_ADDR_PAGE_120 ((uint32_t)0x0800E012)
#define FLASH_ADDR_PAGE_121 ((uint32_t)0x0800E411)
#define FLASH_ADDR_PAGE_122 ((uint32_t)0x0800E810)
#define FLASH_ADDR_PAGE_123 ((uint32_t)0x0800EC10)
#define FLASH_ADDR_PAGE_124 ((uint32_t)0x0801F010)
#define FLASH_ADDR_PAGE_125 ((uint32_t)0x0801F410)
#define FLASH_ADDR_PAGE_126 ((uint32_t)0x0801F810)
#define FLASH_ADDR_PAGE_127 ((uint32_t)0x0801FC00)


#define FLASH_currentspeed_start_addr  FLASH_ADDR_PAGE_126
#define FLASH_currentspeed_end_addr  FLASH_ADDR_PAGE_127 + 0x400 - 0x01


#define FLASH_CW_start_addr FLASH_ADDR_PAGE_124
#define FLASH_CW_end_addr FLASH_ADDR_PAGE_125 + 0x400 - 0x01

#define FLASH_CCW_start_addr FLASH_ADDR_PAGE_122
#define FLASH_CCW_end_addr FLASH_ADDR_PAGE_123 + 0x400 - 0x01 

#define FLASH_BeingHome_start_addr FLASH_ADDR_PAGE_120
#define FLASH_BeingHome_end_addr FLASH_ADDR_PAGE_121 + 0x400 - 0x01 





/* USER CODE END Includes */

/* Private typedef -----------------------------------------------------------*/
/* USER CODE BEGIN PTD */

/* USER CODE END PTD */

/* Private define ------------------------------------------------------------*/
/* USER CODE BEGIN PD */
/* USER CODE END PD */

/* Private macro -------------------------------------------------------------*/
/* USER CODE BEGIN PM */

/* USER CODE END PM */

/* Private variables ---------------------------------------------------------*/
I2C_HandleTypeDef hi2c1;

TIM_HandleTypeDef htim1;
TIM_HandleTypeDef htim2;
TIM_HandleTypeDef htim3;

UART_HandleTypeDef huart1;

/* USER CODE BEGIN PV */
//uint32_t startpage = FLASH_currentspeed__start_addr;
//uint32_t dataread;



int Coating_Menu_Flag = 0;
int Main_menu_flag = 0;
int Speed_menu_flag = 0;
int COF_menu_flag = 0;
int COF_Result_flag = 0;
int COF_Option_Flag = 0;
int COF_Zero_flag = 0;
int COF_Speed_flag = 0;
int COF_Distance_flag = 0;


//Stepper flags
int FWD_Running = 0;
int BWD_Running = 0;

int Coating_Menu_Chosen = 0; // 1: Frequency menu are chosing by the pointer
int COF_Menu_Chosen = 0;  // 1: COF measurament menu are chosing by the pointer

// button flags
int button_A;
int button_B;
int button_C;
int button_D;
int button_E;
int button_F;
int CW_limit = 0;
int CCW_limit = 0;
int CW_COF = 0;
int Stop_State = 1;

//PWM
int Period;


//USB CDC 
uint8_t RxBuffer[64];
uint8_t UsbTxData[8];
uint8_t UsbData[64];

//Freq variable


int T_Duty_Circle = 300;


// speed variables
float current_speed;
int speed = 1000;
int N_currentspeed;
int R_currentspeed;

float Accel_Speed = 0;

int N_SF;
int R_SF;
int N_KF;
int R_KF;

char V[10];
char R[10];

//Button debounce

uint32_t previousMillis = 0;
uint32_t currentMillis = 0;
uint32_t counterOutside = 0; //For testing only
uint32_t counterInside = 0; //For testing only

// COF Variable
uint8_t TxData[8];
uint8_t RxData[32];
uint8_t ZeroData[16];
uint8_t COFData[16];
uint8_t USBSF[8];
uint8_t USBKF[8];
uint8_t USBSD[8];

uint16_t *Data;
int weight = 0;
char strWeight[10];
int Static_peak_delay = 20; // after this, kinetic sample will start calculating
int idx = 0;
int COF_Time = 0;
int Data_Weight[3000];
int Data_Weight_Size = 0;
char Weight_Idx [5];
char K_F[2];
char S_F[2];
int AVG_Weight;
int Static_Weight;
int kinetic_Weight;
int Max_Weight[10];
int Max_Weight_Index[3];
int Max_Weight_idx;

int Stable_Weight_Val;
int Being_home = 0;

int COF_Speed_chosen = 1;
int COF_Distance_chosen = 0;
int COF_Zero_chosen = 0;

int COFPeriod = 3272;
int Speed_COF = 150;
int Distance_COF = 130;
int COF_Lasting;
char COF_Dis[1];

int std_deviation;
float s1;
int K_idx;

/* USER CODE END PV */

/* Private function prototypes -----------------------------------------------*/
void SystemClock_Config(void);
static void MX_GPIO_Init(void);
static void MX_I2C1_Init(void);
static void MX_TIM1_Init(void);
static void MX_USART1_UART_Init(void);
static void MX_TIM2_Init(void);
static void MX_TIM3_Init(void);
/* USER CODE BEGIN PFP */

// a function to get microsecond
void delay_us (uint16_t us)
{
    __HAL_TIM_SET_COUNTER(&htim1,0);  // set the counter value a 0
    while (__HAL_TIM_GET_COUNTER(&htim1) < us);  // wait for the counter to reach the us input in the parameter
} 


//Flag declaration for each type of menu 
void resetbutton()
{
	button_A = 0;
	button_B = 0;
	button_C = 0;
	button_D = 0;
}

void Main_Menu()
{
	Coating_Menu_Flag = 0;
	Main_menu_flag = 1;
	Speed_menu_flag = 0;
	COF_menu_flag = 0;
	COF_Result_flag = 0;
	COF_Option_Flag = 0;
}
void Speed_Menu()
{
	Coating_Menu_Flag = 0;
	Main_menu_flag = 0;
	Speed_menu_flag = 1;
	COF_menu_flag = 0;
	COF_Result_flag = 0;
	COF_Option_Flag = 0;
	COF_Zero_flag = 0;
	COF_Speed_flag = 0;
	COF_Distance_flag = 0;
}
void COF_Menu()
{
	Coating_Menu_Flag = 0;
	Main_menu_flag = 0;
	Speed_menu_flag = 0;
	COF_menu_flag = 1;
	COF_Result_flag = 0;
	COF_Option_Flag = 0;
	COF_Zero_flag = 0;
	COF_Speed_flag = 0;
	COF_Distance_flag = 0;
}
void Coating_Menu()
{
	Coating_Menu_Flag = 1;
	Main_menu_flag = 0;
	Speed_menu_flag = 0;
	COF_menu_flag = 0;
	COF_Result_flag = 0;
	COF_Option_Flag = 0;
	COF_Zero_flag = 0;
	COF_Speed_flag = 0;
	COF_Distance_flag = 0;
}
void COF_Result()
{
	Coating_Menu_Flag = 0;
	Main_menu_flag = 0;
	Speed_menu_flag = 0;
	COF_menu_flag = 0;
	COF_Option_Flag = 0;
	COF_Result_flag = 1;
	COF_Zero_flag = 0;
	COF_Speed_flag = 0;
	COF_Distance_flag = 0;
}
void COF_Options()
{
	Coating_Menu_Flag = 0;
	Main_menu_flag = 0;
	Speed_menu_flag = 0;
	COF_menu_flag = 0;
	COF_Result_flag = 0;
	COF_Option_Flag = 1;
	COF_Zero_flag = 0;
	COF_Speed_flag = 0;
	COF_Distance_flag = 0;
	
}
void COF_Zero()
{
	Coating_Menu_Flag = 0;
	Main_menu_flag = 0;
	Speed_menu_flag = 0;
	COF_menu_flag = 0;
	COF_Result_flag = 0;
	COF_Option_Flag = 0;
	COF_Zero_flag = 1;
	COF_Speed_flag = 0;
	COF_Distance_flag = 0;
}
void COF_Speed()
{
	Coating_Menu_Flag = 0;
	Main_menu_flag = 0;
	Speed_menu_flag = 0;
	COF_menu_flag = 0;
	COF_Result_flag = 0;
	COF_Option_Flag = 0;
	COF_Zero_flag = 0;
	COF_Speed_flag = 1;
	COF_Distance_flag = 0;
}
void COF_Distance()
{
	Coating_Menu_Flag = 0;
	Main_menu_flag = 0;
	Speed_menu_flag = 0;
	COF_menu_flag = 0;
	COF_Result_flag = 0;
	COF_Option_Flag = 0;
	COF_Zero_flag = 0;
	COF_Speed_flag = 0;
	COF_Distance_flag = 1;
}
//void default_F()
//{
//	
//}
void Coating_Speed_Monitor(float T)
{
//	T = T/100;
	N_currentspeed = T/10;
  R_currentspeed = fmod(T,10);
}
void COF_Speed_Monitor(float T)
{
//	T = T/100;
	N_currentspeed = T/1000;
  R_currentspeed = fmod(T,1000)/10;
}
void COF_Distance_Cal(float S, int V)
{
	COF_Lasting = (S/5)*(5/(V/(60*pow(10,3))));
	
}
void COF_Monitor(float SF, float KF)
{
//	SF = SF /1000;
//	KF = KF /1000;
	N_SF = SF/1000;
	R_SF = fmod(SF,1000);
	
	N_KF = KF/1000;
	R_KF = fmod(KF,1000);
}

void Cal_PWM_Period(float speed)
{
	///////////////////////////////////////////////////////////////
	// each turn of vitme equal to 5mm on journey
	// 500 pulse, we have 1 round rotating
	// duty circle = time deploy 5mm / the number of Duty_circle
	///////////////////////////////////////////////////////////////
	
	double t = (5/((speed)/(60*pow(10,6)))); //microsecond
	T_Duty_Circle = (t/4000) ;
	Period = (((T_Duty_Circle*pow(10,-6))*(72*pow(10,6)))/11);
	
	
}
void Cal_COF_Period(float speed)
{
	///////////////////////////////////////////////////////////////
	// each turn of vitme equal to 5mm on journey
	// 500 pulse, we have 1 round rotating
	// duty circle = time deploy 5mm / the number of Duty_circle
	///////////////////////////////////////////////////////////////
	
	double t = (5/((speed)/(60*pow(10,6)))); //microsecond
	T_Duty_Circle = (t/4000) ;
	COFPeriod = (((T_Duty_Circle*pow(10,-6))*(72*pow(10,6)))/11);
	
	
}

////////////////////////////////////////////////////////////////////////
///
///				EEPROM - FLASH save voletive variable
///
///
///
///////////////////////////////////////////////////////////////////////
void FLASH_WritePage(uint32_t startPage,uint32_t endPage, uint32_t data32)
{
	HAL_FLASH_Unlock();
	FLASH_EraseInitTypeDef EraseInit;
	EraseInit.TypeErase = FLASH_TYPEERASE_PAGES;
	EraseInit.PageAddress = startPage;
//	EraseInit.NbPages = 1;
	EraseInit.NbPages = (endPage - startPage + 0x01)/(FLASH_PAGE_SIZE);
	uint32_t PageError = 0;
	HAL_FLASHEx_Erase(&EraseInit,&PageError);
	HAL_FLASH_Program(FLASH_TYPEPROGRAM_WORD, startPage, data32);
	HAL_FLASH_Lock();
}

// Read addr and return val of the address to data variable 
uint32_t FLASH_ReadData32(uint32_t addr)
{
	uint32_t data = *(__IO uint32_t *)(addr);
	return data;
}

void Return_LimitSW_Status()
{
	if(CW_limit) 	// thoat ve man hinh default nhung van giu trang thai cong tac hanh trinh
					{
						button_E = 1;			
						FLASH_WritePage(FLASH_CW_start_addr,FLASH_CW_end_addr,CW_limit);
					}
				else if(CCW_limit)
					{
						button_F = 1;
						FLASH_WritePage(FLASH_CCW_start_addr,FLASH_CCW_end_addr,CCW_limit);
					}
						else
							{
								button_E = 0;
								button_F = 0;
								CW_limit = 0;
								CCW_limit = 0;
								FLASH_WritePage(FLASH_CW_start_addr,FLASH_CW_end_addr,CW_limit);
								FLASH_WritePage(FLASH_CCW_start_addr,FLASH_CCW_end_addr,CCW_limit);
							}
}
void test_1round()
{
	__HAL_TIM_SET_AUTORELOAD(&htim3,900-1);
	HAL_TIM_PWM_Start(&htim3,TIM_CHANNEL_3);
	HAL_Delay(100);
	HAL_TIM_PWM_Stop(&htim3, TIM_CHANNEL_3);
}


////////////////////////////////////////////////////////////////
//
//
//	HMI Handler
//
//
////////////////////////////////////////////////////////////////
void HMI_Main_Menu(_Bool Coating_function,_Bool COF_Measurament)
{
	SSD1306_GotoXY(18,0);
	SSD1306_Puts("COATING - COF",&Font_7x10,0x01);
	SSD1306_GotoXY(0,9);
	SSD1306_Puts("--------------------",&Font_7x10,0x01);
	SSD1306_GotoXY(0,20);
	SSD1306_Puts("Coating Function",&Font_7x10,Coating_function);
	SSD1306_GotoXY(0,32);
	SSD1306_Puts("COF Measuarament",&Font_7x10,COF_Measurament);

//instruction	text
	SSD1306_GotoXY(0,52);
	SSD1306_Puts("a",&Font_7x10,0x00);
	SSD1306_GotoXY(7,52);
	SSD1306_Puts(":Up",&Font_7x10,0x01);
	
	SSD1306_GotoXY(32,52);
	SSD1306_Puts("b",&Font_7x10,0x00);
	SSD1306_GotoXY(39,52);
	SSD1306_Puts(":DWN",&Font_7x10,0x01);
	
	SSD1306_GotoXY(69,52);
	SSD1306_Puts("c",&Font_7x10,0x00);
	SSD1306_GotoXY(76,52);
	SSD1306_Puts(":<",&Font_7x10,0x01);
	
	SSD1306_GotoXY(92,52);
	SSD1306_Puts("d",&Font_7x10,0x00);
	SSD1306_GotoXY(99,52);
	SSD1306_Puts(":Ent",&Font_7x10,0x01);
	
	
	
	SSD1306_UpdateScreen();
}
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
